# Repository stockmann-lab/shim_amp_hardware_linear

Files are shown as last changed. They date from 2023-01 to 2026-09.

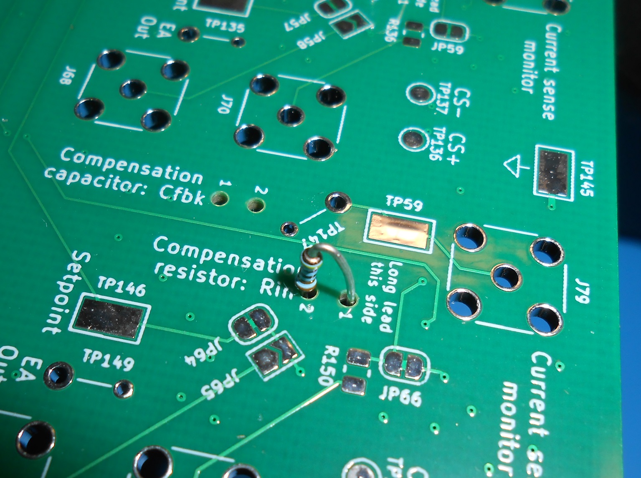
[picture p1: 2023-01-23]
docs/compensation component insertion.JPG

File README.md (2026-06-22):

# MGH open-source shim amplifier repo. 


This repo contains files related to the MGH "Revision D" linear amplifier development (and associated projects).  The shim amplifiers are designed to drive stable currents (up to 4A/channel or more if channels are ganged together in parallel) in shim coils and other inductive loads used for MRI research experiments.  The amplifiers are designed to operate inside the MRI shielded room without causing image degradation due to RF interference.

Content will include design files and bills of materials for both the Printed Circuit Boards (power board, control board, and power distribution board) as well as the mechanical enclosure.

The software and firmware for controlling the shim amplifiers via a Snickerdoodle device can be built from [https://github.com/LincolnCB/rev_d_shim](https://github.com/LincolnCB/rev_d_shim) using the [https://github.com/LincolnCB/zynq_toolbox](https://github.com/LincolnCB/zynq_toolbox) build environment repo.

More details forthcoming.

## Previous shim amplifier projects 

This project builds upon previous work done at MIT-MGH on a Class-AB linear shim amplifier that uses OPA549 op amps in a push-pull configuration.  This previous "Revision C" shim amplifier design is available at:

https://rflab.martinos.org/index.php?title=Current_driver:Current_driver

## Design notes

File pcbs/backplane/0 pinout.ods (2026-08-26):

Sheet: Programmable logic pins
Signal name | Connector pin # | FPGA pin name | FPGA pin | NOTE: I/O Vcc is 3.3V; all signals are LVCMOS
 |  |  |  | Potential problems (signals split between widely separated banks) are in red
JB2 |  |  |  | Active-low signals are preceded by ‘~’
Shutdown_Sense_Sel0 | 4 | IO_0_34 | R19 | Amplifier boards are numbered 0-7
DAC_MISO0 | 5 | IO_L23P_T3_34 | N17
ADC_MISO0 | 7 | IO_L23N_T3_34 | P18 | Signal meanings:
~LDAC0 | 6 | IO_L24N_T3_34 | P16 | SCK is the clock output from the FPGA, to each amplifier board
DAC_MOSI0 | 8 | IO_L24P_T3_34 | P15 | *_LB* are “loopback” signals returned from each amplifier board, to the FPGA (~ADC_CS, and SCK), aligned with the MISO signals
~ADC_CS_LB0 | 11 | IO_L20P_T3_34 | T17
 | 13 | IO_L20N_T3_34 | R18
ADC_MOSI0 | 12 | IO_L19N_T3_VREF_34 | R17 | Signal meanings (aux.):
~ADC_CS0 | 14 | IO_L19P_T3_34 | R16 | Shutdown sense signals, 1 per amplifier board, are latched: these are active when an individual amplifier IC activates on-die over-temp. protection, or when the FPGA forces a manual shutdown
 | 17 | IO_L21P_T3_DQS_34 | V17 | Shutdown_Sense_Sel* signals select an amplifier board’s latched shutdown sense signal to read out on Shutdown_Sense
 | 19 | IO_L21N_T3_DQS_34 | V18 | Power_Enable_FPGA enables the amplifiers when high, and forces a shutdown (and also latches every shutdown sense signal on) on every amplifier board when low
~DAC_CS0 | 18 | IO_L22N_T3_34 | W19 |  | When low, this also resets the DACs & ADCs on the amplifier boards, but only temporarily: this is not latching.
SCK0 | 20 | IO_L22P_T3_34 | W18 | ~Shutdown_Reset clears all the latched shutdown sense signals
 | 23 | IO_L15P_T2_DQS_34 | T20 | Power_Enable_Ext_Sense is high when the manual power-enable control is on, and low when off (all amp boards are forced into shutdown in this case, by backplane circuitry)
 | 25 | IO_L15N_T2_DQS_34 | U20 | Eth_SD is high when signal is detected on optical Ethernet interface
 | 24 | IO_L18N_T2_34 | W16 | Eth_Rx is received data input from optical Ethernet interface
 | 26 | IO_L18P_T2_34 | V16 | Eth_Tx is transmit data output to optical Ethernet interface
 | 29 | IO_L16P_T2_34 | V20
 | 31 | IO_L16N_T2_34 | W20
 | 30 | IO_L17N_T2_34 | Y19
 | 32 | IO_L17P_T2_34 | Y18
SCK_LB0 | 35 | IO_L14P_T2_SRCC_34 | N20
 | 37 | IO_L14N_T2_SRCC_34 | P20
Trigger_In | 36 | IO_L13N_T2_MRCC_34 | P19
10Mhz_In | 38 | IO_L13P_T2_MRCC_34 | N18
JB1
Shutdown_Sense_Sel1 | 4 | IO_25_34 | T19
ADC_MOSI1 | 5 | IO_L1P_T0_34 | T11
~DAC_CS1 | 7 | IO_L1N_T0_34 | T10
~ADC_CS1 | 6 | IO_L2N_T0_34 | U12
DAC_MISO1 | 8 | IO_L2P_T0_34 | T12
SCK1 | 11 | IO_L6P_T0_34 | P14
SCK3 | 13 | IO_L6N_T0_VREF_34 | R14
ADC_MISO1 | 12 | IO_L4N_T0_34 | W13
~ADC_CS_LB1 | 14 | IO_L4P_T0_34 | V12
~DAC_CS3 | 17 | IO_L3P_T0_DQS_PUDC_B_34 | U13
~LDAC3 | 19 | IO_L3N_T0_DQS_34 | V13
DAC_MOSI1 | 18 | IO_L5N_T0_34 | T15
~LDAC1 | 20 | IO_L5P_T0_34 | T14
DAC_MOSI3 | 23 | IO_L9P_T1_DQS_34 | T16
ADC_MOSI3 | 25 | IO_L9N_T1_DQS_34 | U17
 | 24 | IO_L7N_T1_34 | Y17
 | 26 | IO_L7P_T1_34 | Y16
~ADC_CS3 | 29 | IO_L8P_T1_34 | W14
DAC_MISO3 | 31 | IO_L8N_T1_34 | Y14
 | 30 | IO_L10N_T1_34 | W15
~ADC_CS_LB3 | 32 | IO_L10P_T1_34 | V15
SCK_LB3 | 35 | IO_L11P_T1_SRCC_34 | U14
 | 37 | IO_L11N_T1_SRCC_34 | U15
ADC_MISO3 | 36 | IO_L12N_T1_MRCC_34 | U19
SCK_LB1 | 38 | IO_L12P_T1_MRCC_34 | U18
JC1
Shutdown_Sense_Sel2 | 4 | IO_L6N_T0_VREF_13 | V5
SCK_LB2 | 5 | IO_L11P_T1_SRCC_13 | U7
ADC_MOSI2 | 7 | IO_L11N_T1_SRCC_13 | V7
SCK_LB4 | 6 | IO_L12N_T1_MRCC_13 | U10
DAC_MOSI2 | 8 | IO_L12P_T1_MRCC_13 | T9
~ADC_CS2 | 11 | IO_L19P_T3_13 | T5
~ADC_CS_LB2 | 13 | IO_L19N_T3_VREF_13 | U5
~LDAC2 | 12 | IO_L20N_T3_13 | Y13
DAC_MISO4 | 14 | IO_L20P_T3_13 | Y12
ADC_MISO2 | 17 | IO_L21P_T3_DQS_13 | V11
DAC_MISO2 | 19 | IO_L21N_T3_DQS_13 | V10
~ADC_CS_LB4 | 18 | IO_L22N_T3_13 | W6
ADC_MISO4 | 20 | IO_L22P_T3_13 | V6
SCK2 | 23 | IO_L15P_T2_DQS_13 | V8
~DAC_CS2 | 25 | IO_L15N_T2_DQS_13 | W8
~ADC_CS4 | 24 | IO_L18N_T2_13 | Y11
ADC_MOSI4 | 26 | IO_L18P_T2_13 | W11
Eth_SD | 29 | IO_L17P_T2_13 | U9
 | 31 | IO_L17N_T2_13 | U8
DAC_MOSI4 | 30 | IO_L16N_T2_13 | W9
~LDAC4 | 32 | IO_L16P_T2_13 | W10
Eth_Rx | 35 | IO_L14P_T2_SRCC_13 | Y9
Eth_Tx | 37 | IO_L14N_T2_SRCC_13 | Y8
SCK4 | 36 | IO_L13N_T2_MRCC_13 | Y6
~DAC_CS4 | 38 | IO_L13P_T2_MRCC_13 | Y7
JA2
Shutdown_Sense | 4 | IO_25_35 | J15
 | 5 | IO_L22P_T3_AD7P_35 | L14
 | 7 | IO_L22N_T3_AD7N_35 | L15
DAC_MISO6 | 6 | IO_L24N_T3_AD15N_35 | J16
~ADC_CS_LB6 | 8 | IO_L24P_T3_AD15P_35 | K16
 | 11 | IO_L23P_T3_35 | M14
 | 13 | IO_L23N_T3_35 | M15
ADC_MISO6 | 12 | IO_L19N_T3_VREF_35 | G15
~ADC_CS6 | 14 | IO_L19P_T3_35 | H15
 | 17 | IO_L21P_T3_DQS_AD14P_35 | N15
 | 19 | IO_L21N_T3_DQS_AD14N_35 | N16
ADC_MOSI6 | 18 | IO_L20N_T3_AD6N_35 | J14
DAC_MOSI6 | 20 | IO_L20P_T3_AD6P_35 | K14
 | 23 | IO_L9P_T1_DQS_AD3P_35 | L19
 | 25 | IO_L9N_T1_DQS_AD3N_35 | L20
~LDAC6 | 24 | IO_L10N_T1_AD11N_35 | J19
SCK6 | 26 | IO_L10P_T1_AD11P_35 | K19
ADC_MOSI7 | 29 | IO_L8P_T1_AD10P_35 | M17
~ADC_CS_LB7 | 31 | IO_L8N_T1_AD10N_35 | M18
~DAC_CS6 | 30 | IO_L7N_T1_AD2N_35 | M20
 | 32 | IO_L7P_T1_AD2P_35 | M19
SCK_LB7 | 35 | IO_L11P_T1_SRCC_35 | L16
 | 37 | IO_L11N_T1_SRCC_35 | L17
SCK_LB6 | 36 | IO_L12N_T1_MRCC_35 | K18
 | 38 | IO_L12P_T1_MRCC_35 | K17
JA1
~Shutdown_Reset | 4 | IO_0_35 | G14
~ADC_CS5 | 5 | IO_L5P_T0_AD9P_35 | E18
ADC_MOSI5 | 7 | IO_L5N_T0_AD9N_35 | E19
SCK7 | 6 | IO_L4N_T0_35 | D20
~DAC_CS7 | 8 | IO_L4P_T0_35 | D19
DAC_MOSI5 | 11 | IO_L6P_T0_35 | F16
~LDAC5 | 13 | IO_L6N_T0_VREF_35 | F17
~ADC_CS_LB5 | 12 | IO_L1N_T0_AD0N_35 | B20
ADC_MISO5 | 14 | IO_L1P_T0_AD0P_35 | C20
~DAC_CS5 | 17 | IO_L3P_T0_DQS_AD1P_35 | E17
Power_Enable_Ext_Sense | 19 | IO_L3N_T0_DQS_AD1N_35 | D18
DAC_MISO5 | 18 | IO_L2N_T0_AD8N_35 | A20
 | 20 | IO_L2P_T0_AD8P_35 | B19
Power_Enable_FPGA | 23 | IO_L15P_T2_DQS_AD12P_35 | F19
 | 25 | IO_L15N_T2_DQS_AD12N_35 | F20
~LDAC7 | 24 | IO_L18N_T2_AD13N_35 | G20
DAC_MOSI7 | 26 | IO_L18P_T2_AD13P_35 | G19
SCK5 | 29 | IO_L17P_T2_AD5P_35 | J20
 | 31 | IO_L17N_T2_AD5N_35 | H20
ADC_MISO7 | 30 | IO_L16N_T2_35 | G18
~ADC_CS7 | 32 | IO_L16P_T2_35 | G17
 | 35 | IO_L14P_T2_AD4P_SRCC_35 | J18
SCK_LB5 | 37 | IO_L14N_T2_AD4N_SRCC_35 | H18
DAC_MISO7 | 36 | IO_L13N_T2_MRCC_35 | H17
 | 38 | IO_L13P_T2_MRCC_35 | H16

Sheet: CPU peripheral pins
Signal name | Connector pin # | FPGA pin name | FPGA pin | Signal meanings:
 |  |  |  | UART_Tx and UART_Rx are for serial communications to host computer; Tx and Rx are from Snickerdoodle’s perspective
J3 |  |  |  | SDA and SCL are I2C bus to temperature sensors on amplifier boards; no need for clock rates higher than 100 kHz
 | 2 | PS_MIO52_501 | C10 | I2C bus connects to 2x PCA9544 bus expanders: address 1110000 handles amplifier boards 0-3, and 1110001 handles amplifier boards 4-7
 | 4 | PS_MIO53_501 | C11 | Each amplifier board has 3x ADC081C021 ADCs, with addresses 1010101 (left), 1010110 (middle), and 1011001 (right); see schematic for converting ADC readings to temperatures
 | 5 | PS_MIO16_501 | A19
 | 6 | PS_MIO19_501 | D10
 | 7 | PS_MIO17_501 | E14
 | 8 | PS_MIO18_501 | B18
 | 11 | PS_MIO20_501 | A17
 | 12 | PS_MIO23_501 | D11
 | 13 | PS_MIO21_501 | F14
 | 14 | PS_MIO22_501 | B17
 | 17 | PS_MIO24_501 | A16
 | 18 | PS_MIO27_501 | D13
 | 19 | PS_MIO25_501 | F15
 | 20 | PS_MIO26_501 | A15
 | 23 | PS_MIO28_501 | C16
 | 24 | PS_MIO31_501 | E16
 | 25 | PS_MIO29_501 | C13
 | 26 | PS_MIO30_501 | C15
 | 29 | PS_MIO32_501 | A14
 | 30 | PS_MIO35_501 | F12
 | 31 | PS_MIO33_501 | D15
 | 32 | PS_MIO34_501 | A12
UART_Tx | 35 | PS_MIO36_501 | A11
SDA | 36 | PS_MIO39_501 | C18
UART_Rx | 37 | PS_MIO37_501 | A10
SCL | 38 | PS_MIO38_501 | E13

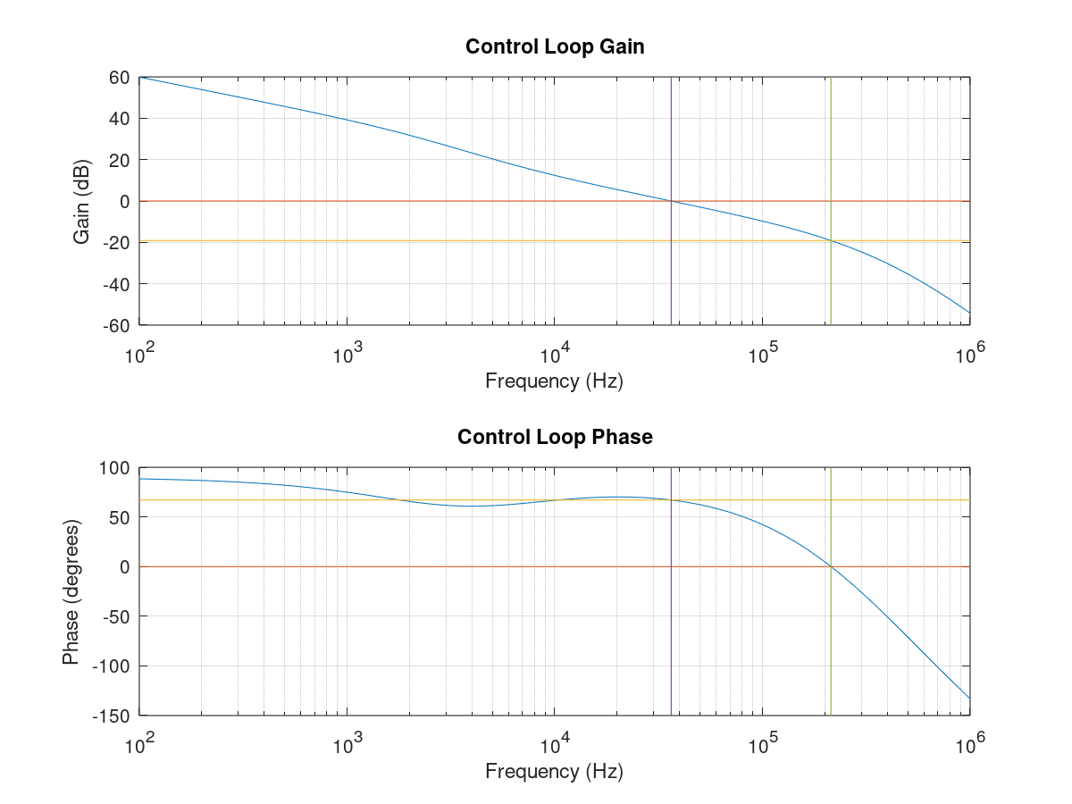
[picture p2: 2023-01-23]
docs/compensation sample output Juchem loop.png

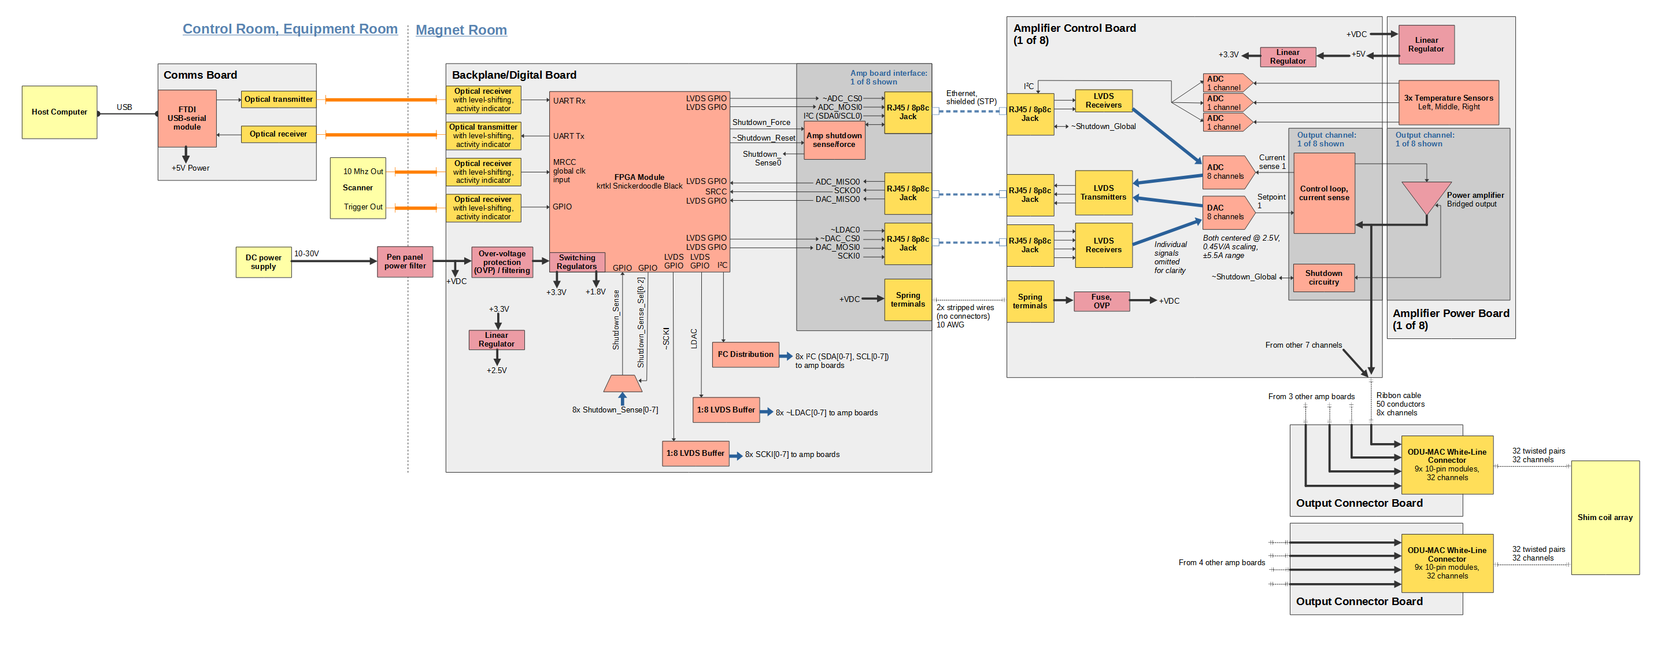
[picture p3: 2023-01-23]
docs/System block diagram.png

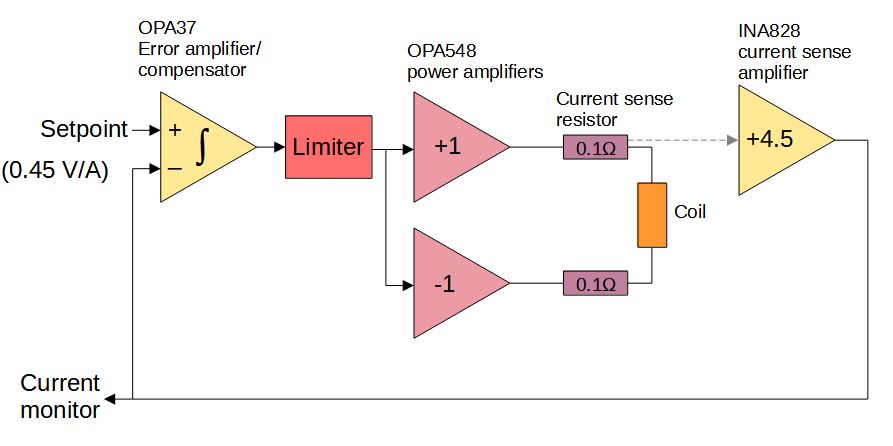
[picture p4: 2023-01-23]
docs/control loop block diagram.png

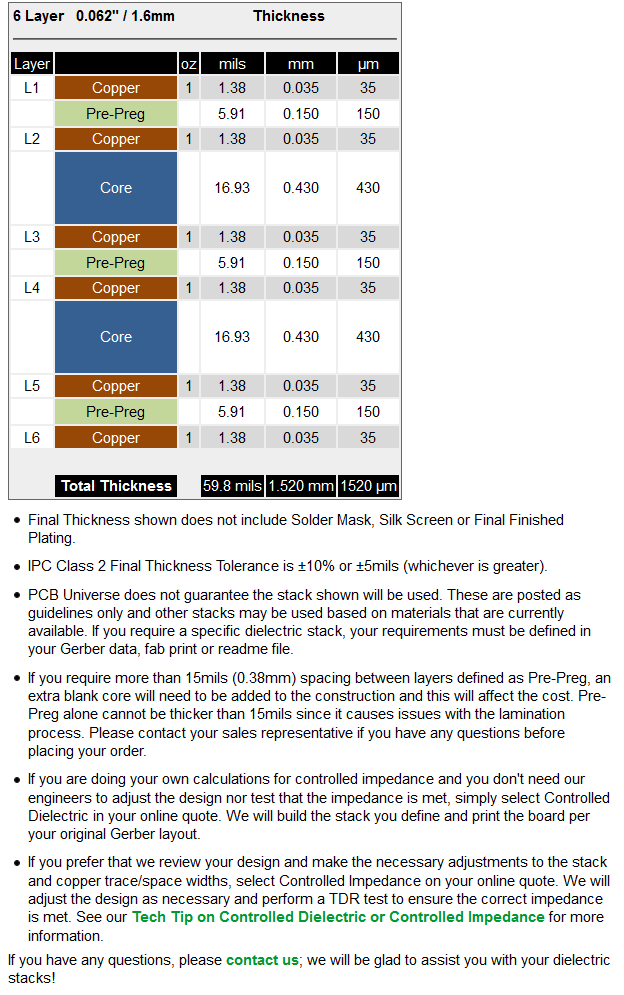
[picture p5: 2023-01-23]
pcbs/backplane/0 stackup, pcb universe.png

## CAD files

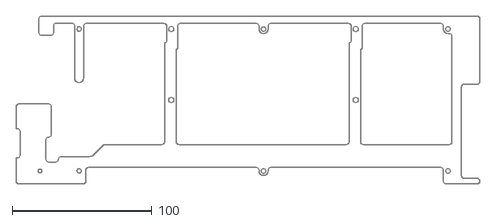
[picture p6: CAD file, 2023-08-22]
pcbs/amp ctrl/manufacturing/amp ctrl-User_StiffenerOutline.dxf
331.8 x 120.0

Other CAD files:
pcbs/amp ctrl/manufacturing/stiffener outline prelim.dxf

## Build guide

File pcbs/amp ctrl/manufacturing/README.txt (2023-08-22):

4 layers, 1.6 mm (0.062") thickness, LPI soldermask and silkscreen both sides
Outer layers 1 oz copper, inner layers 1 oz copper
ENIG plating on pads
Overall dimensions 343.25 x 120 mm (13.514" x 4.724")
Min. trace/spacing 0.16 mm (0.0063")
Min. hole size 0.26 mm (0.010")

All copper layers positive, Gerber RS-247X
*-F_Cu.gtl: Top copper layer 1 (signal)
*-In1_Cu.g2: Copper layer 2 (plane)
*-In2_Cu.g3: Copper layer 3 (plane)
*-B_Cu.gbl: Bottom copper layer 4 (signal)
*-F_Mask.gts: Top soldermask
*-B_Mask.gbs: Bottom soldermask
*-F_SilkS.gto: Top silkscreen
*-B_SilkS.gbo: Bottom silkscreen
*-Edge_Cuts.gm1: Outline
*-PTH.drl: Excellon drill file (plated holes)
*-PTH-drl_map.pdf: Drill map (plated holes)
*-NPTH.drl: Excellon drill file (non-plated holes)
*-NPTH-drl_map.pdf: Drill map (non-plated holes)

*-F_Paste.gtp: Top solder paste
*-B_Paste.gtp: Bottom solder paste
*-AssyTop.pdf: Top-side assembly drawing
*-AssyBot.pdf: Bottom-side assembly drawing
*BOM.xls: Bill of Materials
*.pos, *-pos.csv: Pick-and-place centroid file

Assembly is for bottom-side components only; all top-side components are DNP.
Some pads of DNP components are intentionally excluded from paste layer, please see solder paste Gerber files.

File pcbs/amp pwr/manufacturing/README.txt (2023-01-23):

1-layer Aluminum-core, 1.6 mm thickness with 1 W/(m*K) insulator, 1 oz copper
Lead-free (RoHS) HASL plating on pads, LPI soldermask and silkscreen on top side
Overall dimensions 290 x 110 mm (11.417" x 4.331")
Min. trace/spacing 0.2 mm (0.0079")
Min. hole size 3.2 mm (0.126")
All copper layers positive

*-Edge_Cuts.gm1: Board outline
*-F_Cu.gtl: Top copper
*-F_Mask.gts: Top soldermask
*-F_SilkS.gto: Top silkscreen
*.drl: Drill file (plated holes) - can connect to aluminum core
*-drl_map.pdf: Drill map (plated holes) - can connect to aluminum core
*-Fab.pdf: Fabrication drawing

*-AssyTop.pdf: Assembly drawing
*-F_Paste.gtp: Top solder paste
* BOM.xls: Bill of Materials
*-all.pos, *-all-pos.csv: Pick-and-place centroid component positions

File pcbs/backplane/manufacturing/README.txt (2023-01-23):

6 layers, 1.6 mm (0.062") thickness, LPI soldermask and silkscreen both sides
Outer layers 1 oz copper, inner layers 1 oz copper
ENIG plating on pads
Overall dimensions 145 x 355 mm (5.709" x 13.976")
Min. trace/spacing 0.16 mm (0.0063")
Min. hole size 0.254 mm (0.010")

All copper layers positive, Gerber RS-247X
*-F_Cu.gtl: Top copper layer 1 (mixed signal/plane)
*-In1_Cu.g2: Copper layer 2 (plane)
*-In2_Cu.g3: Copper layer 3 (mixed signal/plane)
*-In3_Cu.g4: Copper layer 4 (plane)
*-In4_Cu.g5: Copper layer 5 (mixed signal/plane)
*-B_Cu.gbl: Bottom copper layer 4 (mixed signal/plane)
*-F_Mask.gts: Top soldermask
*-B_Mask.gbs: Bottom soldermask
*-F_SilkS.gto: Top silkscreen
*-B_SilkS.gbo: Bottom silkscreen
*-Edge_Cuts.gm1: Outline
*-PTH.drl: Excellon drill file (plated holes)
*-PTH-drl_map.pdf: Drill map (plated holes)
*-NPTH.drl: Excellon drill file (non-plated holes)
*-NPTH-drl_map.pdf: Drill map (non-plated holes)

*-F_Paste.gtp: Top solder paste
*-B_Paste.gtp: Bottom solder paste
*-AssyTop.pdf: Top-side assembly drawing
*BOM.xls: Bill of Materials
*.pos, *-pos.csv: Pick-and-place centroid file

All components are on top side.
Exposed copper areas for shielding are intentionally excluded from paste layer, please see solder paste Gerber files.

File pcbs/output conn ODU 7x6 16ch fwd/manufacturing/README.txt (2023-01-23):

4 layers (1-oz copper outer and inner), 1.6 mm (0.062") thickness, LPI green soldermask and white silkscreen both sides, lead-free HASL plating on pads
Overall dimensions 68 x 104 mm (2.677" x 4.095")
All copper layers positive
Min. trace/spacing 0.18 mm (0.007")
Min. hole size > 0.5 mm (0.020")

*-F_Cu.gbr: Top (layer 1) copper
*-In1_Cu.gbr: Layer 2 copper
*-In2_Cu.gbr: Layer 3 copper
*-B_Cu.gbr: Bottom (layer 4) copper
*-F_Mask.gbr: Top soldermask
*-B_Mask.gbr: Bottom soldermask
*-F_SilkS.gbr: Top silkscreen
*-B_SilkS.gbr: Bottom silkscreen
*-Edge_Cuts.gbr: Outline
*-PTH.drl: Drill file (plated holes)
*-NPTH.drl: Drill file (non-plated holes)

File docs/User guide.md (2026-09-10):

# User guide for the linear shim amplifier

## Scaling and data format

Waveforms, as read by the "jm_tool_4board" program on the Snickerdoodle, are stored in CSV (Comma-Separated-Value) files.  There is 1 column for each channel (always with 32 columns; 64 channels are not yet supported in software) and one row per sample / timestep (1 timestep = 20 µs, or 50k samples per second).  Due to a quirk of the software, there needs to be a blank line at the end of the file to work properly.

Each data point is a number from 0 to 65535.  32768 corresponds to zero current, while lower numbers represent a negative current and higher numbers represent a positive current.  The scaling is about 0.1528 mA per count, for ±5.007A total.  The output current should not be set beyond ±4A due to limitations of the driver ICs, but the extra range is useful for reading overshoot and other transient effects.

The control voltages produced by the DAC are centered at about 2.048V (= zero current), with a range of 0-4.096V (2.048V ± 2.048V) and a scaling of 0.409 V/A, or 2.445 A/V for the output current.  When the system is idle (no current commanded through any coil), you should see 2.048V (± a couple mV) at every DAC output.

## Using external analog setpoints

Instead of using the DAC & digital controls, analog setpoints can also be sent to each channel directly through an SMA coax connector.  There are two separate modes:
(Components to populate are listed for channel 1 only on amp control board: see schematic for equivalents on other channels)
- **Without level shifter:** 2.048V = 0A, input range is 0V - 4.096V.  Populate J2, R236, R237; close jumpers JP87, JP16; open jumper JP15.
- **With level shifter:** 0V = 0A, input range is -2.048V - +2.048V.  Populate J2, R237, RN5-6, R343, C273, U73; close jumper JP16; open jumper JP15.  Signal source needs to be low-impedance, such as a 50Ω output from a function generator, to avoid creating excessive errors in offset & scaling.  If particularly low offset current is needed (under 5.6 mA), R343 can provide some adjustment range (see schematic).
In both cases, scaling is 0.4049 V/A = 2.4697 A/V.

## Misc. details for testing & development

### Connections

When powering up an incomplete system for testing, some caveats to be aware of:
- **Ethernet cable types:** Only use shielded Ethernet cables (distinguished by the metal shields on the connectors) for connecting the backplane to the amplifier boards: they use this not just for EMI, but for the backplane's control ground connection.
- **Backplane power:** The backplane gets its control-ground connection through the amplifier boards, specifically their Ethernet cables.  So if no amplifier boards are connected to the backplane via Ethernet cables, or they don't use _shielded_ Ethernet cables, then the backplane's Snickerdoodle will not have power.  For testing the backplane alone, you can connect a jumper wire from one of the amplifier-power connector's "-" sides to any of the "GND" testpoints on the backplane.  (This was done to avoid ground loops, but may be rethought after more EMI testing)
- **Amplifier control board power:** Each amplifier board stack (control & power board) has its 5V regulator, for the digital control circuitry, located on the amplifier power board for heatsinking.  If using the amplifier control board _without_ a power board attached, there will be no power to the ADC or DAC.  Either connect the amplifier control board to a power board, or make a small substitute regulator for testing, based on a 2x2 male header and a 7805 voltage regulator (see layout for pinout).

### Amplifier board final assembly

After 3rd-party assembly of all SMT parts, the through-hole parts to add manually are...
- Phoenix 1190363 **power connector** _(1x)_
- TE Connectivity 1-406541-8, or 1-406541-5, or 2-406541-1 **RJ-45 connectors** _(3x)_
See design files & BOM for component locations and details.

### Backplane board final assembly

After 3rd-party assembly of all SMT parts, the parts to add manually are...
- Phoenix 11903633 **power connectors for amplifier boards** _(1x/connected amplifier board)_
- Amphenol-ICC RJE061881120 or RJE061881120H **RJ-45 connectors** _(3x/connected amplifier board)_
- Samtec TFM-115-01-S-D-WT, or TFM-115-01-L-D-WT, or TFM-115-01-F-D-WT **Snickerdoodle connector** _(1x)_
- Samtec TFM-120-01-S-D-WT, or TFM-120-01-L-D-WT, or TFM-120-01-F-D-WT **Snickerdoodle connector** _(6x)_
- Avago AFBR-2624Z **optical receiver** _(4x)_
- Avago AFBR-1624Z **optical transmitter** _(1x)_
- ON Semi D44H11G **power transistor** _(1x)_
- CTS 7-340-1PP-BA **heatsink for power transistor** _(1x)_
See design files & BOM for component locations and details.

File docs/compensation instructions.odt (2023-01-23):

Current Drivers Rev. D

Control Loop Compensation Adjustment

Don Straney

dstraney@mgh.harvard.edu

2021-07-08

# Instructions

1. Measure the inductance and series resistance of your coil, including all cabling, using an LCR meter such as the Keysight U1733C. 100 kHz (or 10 kHz if your LCR meter doesn’t reach 100 kHz) is the preferred measurement frequency, as this is in the general range of where the control loop crossover will be.
2. Open “compensation.m” and change the values next to “Rload” and “Lload” to match your measured coil parameters.
3. If you are using MATLAB instead of GNU Octave, comment the “pkg load control” line.
4. Save and close, then run the script in MATLAB or Octave. It should produce two figures, one showing the loop frequency response and one with step response, and output text describing the component values. This is the sample output for a 723µH + 10Ω coil:

Rin total value: 108.5 ohms
Rin value to install: 8.5 ohms (closest E24 is 8.2 ohms, error of 0.3%)
Cfbk total value: 1313 pF
Cfbk value to install: 1293 pF (closest E12 is 1200 pF, error of 7.1%)
Max. load capacitance across coil: 265 pF
------------
Phase margin: 67.1 degrees @ 36360 Hz crossover
Gain margin: 19.1 dB @ 213732 Hz
------------
Min. Rin value, constrained by error amplifier BW: 108.5 ohms
Load pole: 2245.34 Hz
Error amplifier zero: 6062.42 Hz
Error amplifier GBP pole: 238797 Hz
Predicted parasitic PCB-feedback-capacitance pole: 3.97887e+06 Hz
Vout_cmd filter pole: 4.97359e+06 Hz
------------
1% settling time: 6.51e-05 s
0.1% settling time: 1.18e-04 s
1% settling time with LPF: 7.69e-05 s
0.1% settling time with LPF: 9.87e-05 s

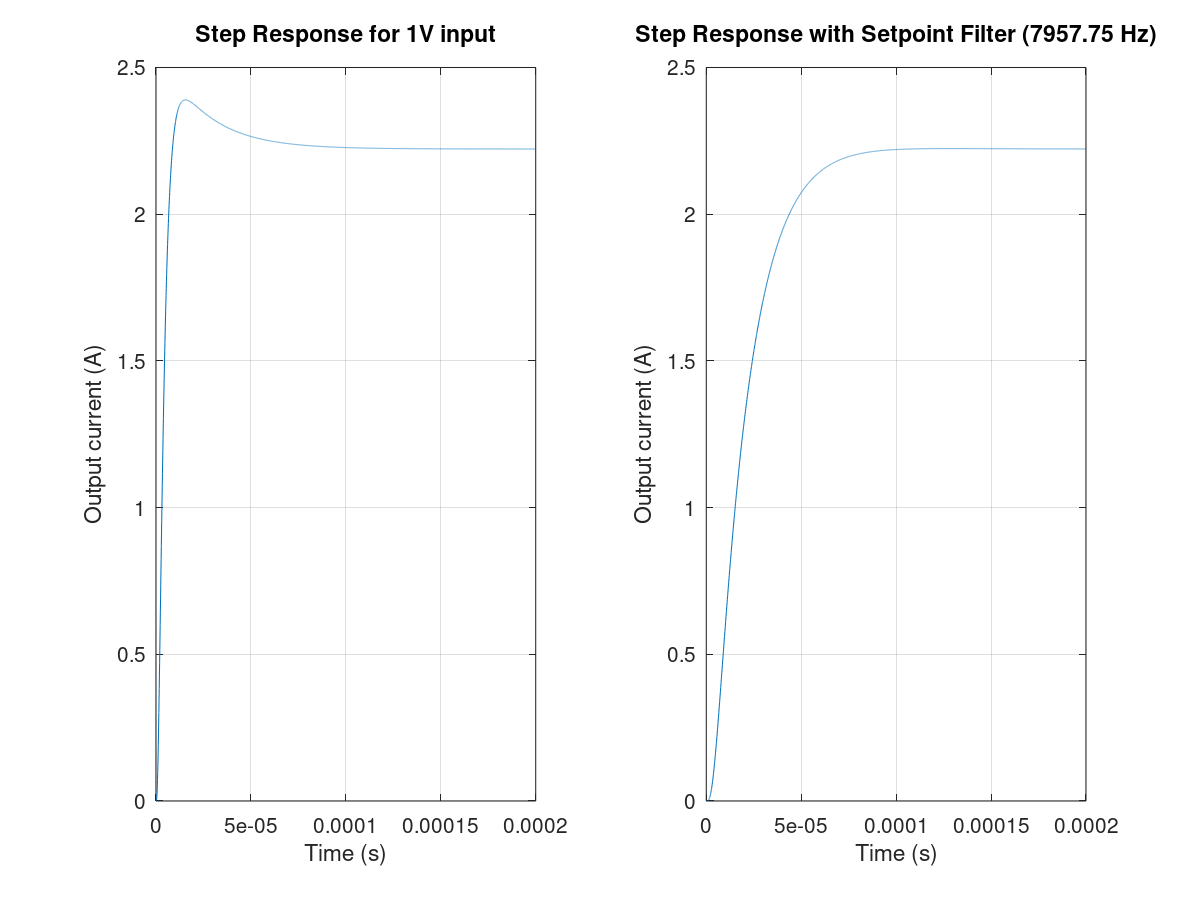
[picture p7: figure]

# Using the Results

Compensation components: There are two components you will need to install for every channel: one resistor (“Rin”) and one capacitor (“Cfbk”), with the values given here (“closest E12…” and “closest E24…”). You will need to have through-hole components with these values; for the capacitor, use 50V NP0/C0G ceramic parts with a 0.1”/2.54 mm lead spacing, and for the resistor, use a metal film (not carbon composition) 1/8W / 0204-size part for easiest insertion.

If the Cfbk value to install is < 10 pF, don’t install a capacitor. If the Rin value to install is < 5Ω, install a jumper instead (U-shaped piece of 24-26 AWG solid bare wire). Fold one of the resistor leads back over the body. Trim all leads to ~1 cm maximum away from the body.

Insert these components into the labeled sets of holes in the amp control board, from the top (outward-facing) side:

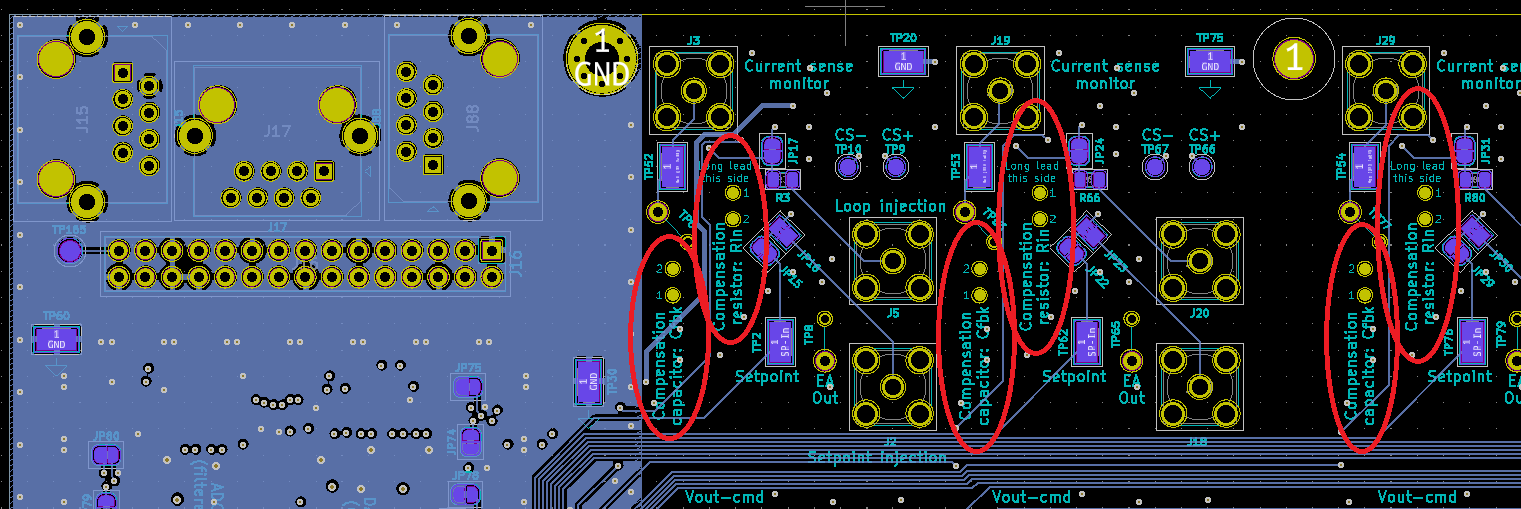
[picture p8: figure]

Make sure to insert the resistor in the orientation described, with the longer lead facing the edge of the board and the body facing the interior of the board. This orientation puts less conductor area on the inverting node of the error amplifier and potentially reduces destabilizing parasitic capacitance and coupling from other channels/noise sources.

Capacitance across coil: Shim coils will often have one or more filter capacitors placed across their leads at some point in the cabling, either to prevent transmitted RF from traveling out of the scanner’s bore along the shim cables, or to prevent RF noise outside the scanner from travelling into the bore along the shim cables. The maximum value of this capacitance is limited in practice by the resonance it creates with the shim coil’s inductance, which causes various effects that erode the gain margin and therefore stability of the control loop. The compensation script makes a general prediction of the maximum coil capacitance allowed, and prints it as “Max. load capacitance across coil” (265 pF in the example above). Do not use more than this total allowed capacitance (including feed-through filters, multiple capacitors, etc.) across your shim coil.

Settling time: The “settling time” values printed show how long it will take after each change of output current setpoint (not including the delay for digital communications) for the output current to settle to within either 1% or 0.1% of the final value.

# Slew-Rate Limiting

Some applications will want to limit the slew rate when changing the output current, to reduce the movement and auditory noise created by the force on the coil in the scanner’s magnetic field. This is best handled by software, but if for various reasons a hardware low-pass filter (LPF) is needed on the current setpoint, the effect on the step response can be predicted by the compensation script.

The “Rsplpf” and “Csplpf” variables in “compensation.m” set the parameters for a single-pole RC filter. When “compensation.m” is run, the right-most step response plot (titled “...with Setpoint Filter”) will show the modified step response with the LPF present. The second set of settling times printed (“...with LPF:”) shows the settling times with the LPF present.

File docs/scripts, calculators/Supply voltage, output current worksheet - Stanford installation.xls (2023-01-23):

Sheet: Main
Parameters
Load resistance |  |  | Calculations
Cable resistance (total) | 0.477 | Ω | Cable length | 4.5 | m | Kawin coil’s main/longest cable w/thinner wire is ~13.5’/4.5m 22 AWG and measures 0.24Ω max. per conductor
 |  |  | Wire gauge | 22 | AWG
 |  |  | Predicted cable resistance (per conductor) | 0.2385 | Ω
RF choke resistance (total) | 0.185 | Ω | RF choke resistance (each) | 0.037 | Ω | 3T toroid measured
 |  |  | Number of RF chokes, max. | 5
Coil resistance | 0.05 | Ω |  |  |  | Guess
Total load resistance | 0.712 | Ω
Shim amp
Output cable resistance (total) | 0.138 | Ω | Ribbon cable length | 0.5 | m | Overly long cable used in test setup; not far off from 0.16Ω measured (including a couple in. of 24AWG, “output connector PCB” traces, and Molex Mini-Fit Jr. connector)
 |  |  | Ribbon cable wire gauge | 28 | AWG
 |  |  | Number of parallel strands | 3
 |  |  | Predicted ribbon cable resistance (total) | 0.071 | Ω
 |  |  | Connector contact resistance (per pin) | 0.05 | Ω | Educated guess based on past measurements
 |  |  | Predicted connector resistance (total) | 0.067 | Ω
Output onboard resistance | 0.379 | Ω | Current sense resistor value | 0.1 | Ω
Total shim amp per-channel resistance | 0.517 | Ω | Total current sense resistance | 0.2 | Ω
 |  |  | PCB trace resistance (single conductor) | 0.073 |  | Worst case is channel 1: 270 mm of 1.8 mm wide traces in 1 oz copper
 |  |  | Connector contact resistance (per pin) | 0.05 |  | Educated guess based on past measurements
 |  |  | Number of parallel pins | 3
 |  |  | Total parasitic resistances to output connector | 0.179 | Ω
Power cable resistance | 0.02726666667 | Ω | Cable length | 10 | m
 |  |  | Wire gauge | 6 | AWG
 |  |  | Predicted cable resistance (per conductor) | 0.01296 | Ω
 |  |  | Backplane PCB resistance | 0.000673 | Ω | Very conservative estimate, 65 mm wide (min., wider at top) x 135 mm long (to furthest connector) on 3x 0.5 oz copper layers (at least one is actually 1 oz)
Internal power cabling resistance | 0.0052 | Ω | Cable length | 0.5 | m
Total shim amp input power resistance | 0.03246666667 | Ω | Wire gauge | 12 | AWG
 |  |  | Predicted cable resistance (per conductor) | 0.0026 | Ω
Minimum Vcc from known Iout
Desired output current per channel | 4 | A
Max. instantaneous total output current on all channels combined | 40 | A
Vcc @ OPA548 | 15.06 | V
Sag on power cable | 1.091 | V
Sag on internal power cabling | 0.208 | V
Min. Vcc | 16.4 | V

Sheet: Reference
AWG | Diameter (mm) | Ω/m
34 | 0.16 | 0.856
32 | 0.2032 | 0.538
30 | 0.254 | 0.338
28 | 0.32 | 0.213
26 | 0.404 | 0.134
24 | 0.511 | 0.084
22 | 0.645 | 0.053
20 | 0.813 | 0.033
18 | 1.024 | 0.021
16 | 1.29 | 0.013
14 | 1.628 | 0.0083
12 | 2.052 | 0.0052
10 | 2.588 | 0.0033
8 | 3.264 | 0.00206
6 | 4.115 | 0.001296
4 | 5.189 | 0.000815
2 | 6.543 | 0.000156
Extracted from OPA548 datasheet, figure 13 Fit to 3rd-order polynomial and extrapolated beyond 4A Temperature-based multiplication factor comes from increase in headroom @ 3A out (figure 14) This temperature multiplier is actually negative at a lower current (0.6A out), so may be even larger @ Iout > 3A
Output current (A) | Voltage headroom (V) | Voltage headroom @ 100 C (V) | Headroom multiplication factor:
0.1 | 1.703623124 | 1.826390744 | 1.072
0.2 | 1.773639595 | 1.901452787
0.3 | 1.842929576 | 1.975735989
0.4 | 1.911584312 | 2.049338169
0.5 | 1.979695048 | 2.122357146
0.6 | 2.047353029 | 2.19489074
0.7 | 2.114649497 | 2.267036772
0.8 | 2.181675699 | 2.33889306
0.9 | 2.248522878 | 2.410557425
1 | 2.31528228 | 2.482127687
1.1 | 2.382045147 | 2.553701665
1.2 | 2.448902726 | 2.625377178
1.3 | 2.51594626 | 2.697252048
1.4 | 2.583266994 | 2.769424093
1.5 | 2.650956172 | 2.841991134
1.6 | 2.719105039 | 2.915050989
1.7 | 2.787804839 | 2.98870148
1.8 | 2.857146816 | 3.063040425
1.9 | 2.927222216 | 3.138165645
2 | 2.998122283 | 3.214174959
2.1 | 3.06993826 | 3.291166187
2.2 | 3.142761393 | 3.369237149
2.3 | 3.216682926 | 3.448485665
2.4 | 3.291794104 | 3.529009554
2.5 | 3.36818617 | 3.610906636
2.6 | 3.44595037 | 3.694274731
2.7 | 3.525177948 | 3.779211659
2.8 | 3.605960148 | 3.865815239
2.9 | 3.688388214 | 3.954183292
3 | 3.772553392 | 4.044413637
3.1 | 3.858546926 | 4.136604093
3.2 | 3.94646006 | 4.230852482
3.3 | 4.036384038 | 4.327256622
3.4 | 4.128410106 | 4.425914333
3.5 | 4.222629507 | 4.526923435
3.6 | 4.319133486 | 4.630381747
3.7 | 4.418013287 | 4.736387091
3.8 | 4.519360156 | 4.845037284
3.9 | 4.623265335 | 4.956430148
4 | 4.729820071 | 5.070663502
4.1 | 4.839115607 | 5.187835165
4.2 | 4.951243188 | 5.308042958
4.3 | 5.066294058 | 5.4313847
4.4 | 5.184359462 | 5.557958212
4.5 | 5.305530644 | 5.687861312
4.6 | 5.429898848 | 5.82119182
4.7 | 5.55755532 | 5.958047557
4.8 | 5.688591303 | 6.098526343
4.9 | 5.823098043 | 6.242725996
5 | 5.961166783 | 6.390744337

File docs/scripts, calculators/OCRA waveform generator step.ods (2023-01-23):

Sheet: Params
Amplitude | -1.5 | A
Length | 2.00E-02 | sec
Length, calculated | 999 | samples
Channel #, min. | 8 | (1-32)
Channel #, max. | 8 | (1-32)
Timestep | 2.00E-05 | sec
Vref | 2.5 | V
Scaling factor | 0.449201 | V/A
NOTE: Tab separators are ok, but output file needs space at end of last text line

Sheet: Amplitudes (A)
0 | 0 | 0 | 0 | 0 | 0 | 0 | -1.5 | 0 | 0 | 0 | 0 | 0 | 0 | 0 | 0 | 0 | 0 | 0 | 0 | 0 | 0 | 0 | 0 | 0 | 0 | 0 | 0 | 0 | 0 | 0 | 0
0 | 0 | 0 | 0 | 0 | 0 | 0 | -1.5 | 0 | 0 | 0 | 0 | 0 | 0 | 0 | 0 | 0 | 0 | 0 | 0 | 0 | 0 | 0 | 0 | 0 | 0 | 0 | 0 | 0 | 0 | 0 | 0
0 | 0 | 0 | 0 | 0 | 0 | 0 | -1.5 | 0 | 0 | 0 | 0 | 0 | 0 | 0 | 0 | 0 | 0 | 0 | 0 | 0 | 0 | 0 | 0 | 0 | 0 | 0 | 0 | 0 | 0 | 0 | 0
0 | 0 | 0 | 0 | 0 | 0 | 0 | -1.5 | 0 | 0 | 0 | 0 | 0 | 0 | 0 | 0 | 0 | 0 | 0 | 0 | 0 | 0 | 0 | 0 | 0 | 0 | 0 | 0 | 0 | 0 | 0 | 0
0 | 0 | 0 | 0 | 0 | 0 | 0 | -1.5 | 0 | 0 | 0 | 0 | 0 | 0 | 0 | 0 | 0 | 0 | 0 | 0 | 0 | 0 | 0 | 0 | 0 | 0 | 0 | 0 | 0 | 0 | 0 | 0
0 | 0 | 0 | 0 | 0 | 0 | 0 | -1.5 | 0 | 0 | 0 | 0 | 0 | 0 | 0 | 0 | 0 | 0 | 0 | 0 | 0 | 0 | 0 | 0 | 0 | 0 | 0 | 0 | 0 | 0 | 0 | 0
0 | 0 | 0 | 0 | 0 | 0 | 0 | -1.5 | 0 | 0 | 0 | 0 | 0 | 0 | 0 | 0 | 0 | 0 | 0 | 0 | 0 | 0 | 0 | 0 | 0 | 0 | 0 | 0 | 0 | 0 | 0 | 0
0 | 0 | 0 | 0 | 0 | 0 | 0 | -1.5 | 0 | 0 | 0 | 0 | 0 | 0 | 0 | 0 | 0 | 0 | 0 | 0 | 0 | 0 | 0 | 0 | 0 | 0 | 0 | 0 | 0 | 0 | 0 | 0
0 | 0 | 0 | 0 | 0 | 0 | 0 | -1.5 | 0 | 0 | 0 | 0 | 0 | 0 | 0 | 0 | 0 | 0 | 0 | 0 | 0 | 0 | 0 | 0 | 0 | 0 | 0 | 0 | 0 | 0 | 0 | 0
0 | 0 | 0 | 0 | 0 | 0 | 0 | -1.5 | 0 | 0 | 0 | 0 | 0 | 0 | 0 | 0 | 0 | 0 | 0 | 0 | 0 | 0 | 0 | 0 | 0 | 0 | 0 | 0 | 0 | 0 | 0 | 0
0 | 0 | 0 | 0 | 0 | 0 | 0 | -1.5 | 0 | 0 | 0 | 0 | 0 | 0 | 0 | 0 | 0 | 0 | 0 | 0 | 0 | 0 | 0 | 0 | 0 | 0 | 0 | 0 | 0 | 0 | 0 | 0
0 | 0 | 0 | 0 | 0 | 0 | 0 | -1.5 | 0 | 0 | 0 | 0 | 0 | 0 | 0 | 0 | 0 | 0 | 0 | 0 | 0 | 0 | 0 | 0 | 0 | 0 | 0 | 0 | 0 | 0 | 0 | 0
0 | 0 | 0 | 0 | 0 | 0 | 0 | -1.5 | 0 | 0 | 0 | 0 | 0 | 0 | 0 | 0 | 0 | 0 | 0 | 0 | 0 | 0 | 0 | 0 | 0 | 0 | 0 | 0 | 0 | 0 | 0 | 0
0 | 0 | 0 | 0 | 0 | 0 | 0 | -1.5 | 0 | 0 | 0 | 0 | 0 | 0 | 0 | 0 | 0 | 0 | 0 | 0 | 0 | 0 | 0 | 0 | 0 | 0 | 0 | 0 | 0 | 0 | 0 | 0
0 | 0 | 0 | 0 | 0 | 0 | 0 | -1.5 | 0 | 0 | 0 | 0 | 0 | 0 | 0 | 0 | 0 | 0 | 0 | 0 | 0 | 0 | 0 | 0 | 0 | 0 | 0 | 0 | 0 | 0 | 0 | 0
0 | 0 | 0 | 0 | 0 | 0 | 0 | -1.5 | 0 | 0 | 0 | 0 | 0 | 0 | 0 | 0 | 0 | 0 | 0 | 0 | 0 | 0 | 0 | 0 | 0 | 0 | 0 | 0 | 0 | 0 | 0 | 0
0 | 0 | 0 | 0 | 0 | 0 | 0 | -1.5 | 0 | 0 | 0 | 0 | 0 | 0 | 0 | 0 | 0 | 0 | 0 | 0 | 0 | 0 | 0 | 0 | 0 | 0 | 0 | 0 | 0 | 0 | 0 | 0
0 | 0 | 0 | 0 | 0 | 0 | 0 | -1.5 | 0 | 0 | 0 | 0 | 0 | 0 | 0 | 0 | 0 | 0 | 0 | 0 | 0 | 0 | 0 | 0 | 0 | 0 | 0 | 0 | 0 | 0 | 0 | 0
0 | 0 | 0 | 0 | 0 | 0 | 0 | -1.5 | 0 | 0 | 0 | 0 | 0 | 0 | 0 | 0 | 0 | 0 | 0 | 0 | 0 | 0 | 0 | 0 | 0 | 0 | 0 | 0 | 0 | 0 | 0 | 0
0 | 0 | 0 | 0 | 0 | 0 | 0 | -1.5 | 0 | 0 | 0 | 0 | 0 | 0 | 0 | 0 | 0 | 0 | 0 | 0 | 0 | 0 | 0 | 0 | 0 | 0 | 0 | 0 | 0 | 0 | 0 | 0
0 | 0 | 0 | 0 | 0 | 0 | 0 | -1.5 | 0 | 0 | 0 | 0 | 0 | 0 | 0 | 0 | 0 | 0 | 0 | 0 | 0 | 0 | 0 | 0 | 0 | 0 | 0 | 0 | 0 | 0 | 0 | 0
0 | 0 | 0 | 0 | 0 | 0 | 0 | -1.5 | 0 | 0 | 0 | 0 | 0 | 0 | 0 | 0 | 0 | 0 | 0 | 0 | 0 | 0 | 0 | 0 | 0 | 0 | 0 | 0 | 0 | 0 | 0 | 0
0 | 0 | 0 | 0 | 0 | 0 | 0 | -1.5 | 0 | 0 | 0 | 0 | 0 | 0 | 0 | 0 | 0 | 0 | 0 | 0 | 0 | 0 | 0 | 0 | 0 | 0 | 0 | 0 | 0 | 0 | 0 | 0
0 | 0 | 0 | 0 | 0 | 0 | 0 | -1.5 | 0 | 0 | 0 | 0 | 0 | 0 | 0 | 0 | 0 | 0 | 0 | 0 | 0 | 0 | 0 | 0 | 0 | 0 | 0 | 0 | 0 | 0 | 0 | 0
0 | 0 | 0 | 0 | 0 | 0 | 0 | -1.5 | 0 | 0 | 0 | 0 | 0 | 0 | 0 | 0 | 0 | 0 | 0 | 0 | 0 | 0 | 0 | 0 | 0 | 0 | 0 | 0 | 0 | 0 | 0 | 0
0 | 0 | 0 | 0 | 0 | 0 | 0 | -1.5 | 0 | 0 | 0 | 0 | 0 | 0 | 0 | 0 | 0 | 0 | 0 | 0 | 0 | 0 | 0 | 0 | 0 | 0 | 0 | 0 | 0 | 0 | 0 | 0
0 | 0 | 0 | 0 | 0 | 0 | 0 | -1.5 | 0 | 0 | 0 | 0 | 0 | 0 | 0 | 0 | 0 | 0 | 0 | 0 | 0 | 0 | 0 | 0 | 0 | 0 | 0 | 0 | 0 | 0 | 0 | 0
0 | 0 | 0 | 0 | 0 | 0 | 0 | -1.5 | 0 | 0 | 0 | 0 | 0 | 0 | 0 | 0 | 0 | 0 | 0 | 0 | 0 | 0 | 0 | 0 | 0 | 0 | 0 | 0 | 0 | 0 | 0 | 0
0 | 0 | 0 | 0 | 0 | 0 | 0 | -1.5 | 0 | 0 | 0 | 0 | 0 | 0 | 0 | 0 | 0 | 0 | 0 | 0 | 0 | 0 | 0 | 0 | 0 | 0 | 0 | 0 | 0 | 0 | 0 | 0
0 | 0 | 0 | 0 | 0 | 0 | 0 | -1.5 | 0 | 0 | 0 | 0 | 0 | 0 | 0 | 0 | 0 | 0 | 0 | 0 | 0 | 0 | 0 | 0 | 0 | 0 | 0 | 0 | 0 | 0 | 0 | 0
0 | 0 | 0 | 0 | 0 | 0 | 0 | -1.5 | 0 | 0 | 0 | 0 | 0 | 0 | 0 | 0 | 0 | 0 | 0 | 0 | 0 | 0 | 0 | 0 | 0 | 0 | 0 | 0 | 0 | 0 | 0 | 0
0 | 0 | 0 | 0 | 0 | 0 | 0 | -1.5 | 0 | 0 | 0 | 0 | 0 | 0 | 0 | 0 | 0 | 0 | 0 | 0 | 0 | 0 | 0 | 0 | 0 | 0 | 0 | 0 | 0 | 0 | 0 | 0
0 | 0 | 0 | 0 | 0 | 0 | 0 | -1.5 | 0 | 0 | 0 | 0 | 0 | 0 | 0 | 0 | 0 | 0 | 0 | 0 | 0 | 0 | 0 | 0 | 0 | 0 | 0 | 0 | 0 | 0 | 0 | 0
0 | 0 | 0 | 0 | 0 | 0 | 0 | -1.5 | 0 | 0 | 0 | 0 | 0 | 0 | 0 | 0 | 0 | 0 | 0 | 0 | 0 | 0 | 0 | 0 | 0 | 0 | 0 | 0 | 0 | 0 | 0 | 0
0 | 0 | 0 | 0 | 0 | 0 | 0 | -1.5 | 0 | 0 | 0 | 0 | 0 | 0 | 0 | 0 | 0 | 0 | 0 | 0 | 0 | 0 | 0 | 0 | 0 | 0 | 0 | 0 | 0 | 0 | 0 | 0
0 | 0 | 0 | 0 | 0 | 0 | 0 | -1.5 | 0 | 0 | 0 | 0 | 0 | 0 | 0 | 0 | 0 | 0 | 0 | 0 | 0 | 0 | 0 | 0 | 0 | 0 | 0 | 0 | 0 | 0 | 0 | 0
0 | 0 | 0 | 0 | 0 | 0 | 0 | -1.5 | 0 | 0 | 0 | 0 | 0 | 0 | 0 | 0 | 0 | 0 | 0 | 0 | 0 | 0 | 0 | 0 | 0 | 0 | 0 | 0 | 0 | 0 | 0 | 0
0 | 0 | 0 | 0 | 0 | 0 | 0 | -1.5 | 0 | 0 | 0 | 0 | 0 | 0 | 0 | 0 | 0 | 0 | 0 | 0 | 0 | 0 | 0 | 0 | 0 | 0 | 0 | 0 | 0 | 0 | 0 | 0
0 | 0 | 0 | 0 | 0 | 0 | 0 | -1.5 | 0 | 0 | 0 | 0 | 0 | 0 | 0 | 0 | 0 | 0 | 0 | 0 | 0 | 0 | 0 | 0 | 0 | 0 | 0 | 0 | 0 | 0 | 0 | 0
0 | 0 | 0 | 0 | 0 | 0 | 0 | -1.5 | 0 | 0 | 0 | 0 | 0 | 0 | 0 | 0 | 0 | 0 | 0 | 0 | 0 | 0 | 0 | 0 | 0 | 0 | 0 | 0 | 0 | 0 | 0 | 0
0 | 0 | 0 | 0 | 0 | 0 | 0 | -1.5 | 0 | 0 | 0 | 0 | 0 | 0 | 0 | 0 | 0 | 0 | 0 | 0 | 0 | 0 | 0 | 0 | 0 | 0 | 0 | 0 | 0 | 0 | 0 | 0
0 | 0 | 0 | 0 | 0 | 0 | 0 | -1.5 | 0 | 0 | 0 | 0 | 0 | 0 | 0 | 0 | 0 | 0 | 0 | 0 | 0 | 0 | 0 | 0 | 0 | 0 | 0 | 0 | 0 | 0 | 0 | 0
0 | 0 | 0 | 0 | 0 | 0 | 0 | -1.5 | 0 | 0 | 0 | 0 | 0 | 0 | 0 | 0 | 0 | 0 | 0 | 0 | 0 | 0 | 0 | 0 | 0 | 0 | 0 | 0 | 0 | 0 | 0 | 0
0 | 0 | 0 | 0 | 0 | 0 | 0 | -1.5 | 0 | 0 | 0 | 0 | 0 | 0 | 0 | 0 | 0 | 0 | 0 | 0 | 0 | 0 | 0 | 0 | 0 | 0 | 0 | 0 | 0 | 0 | 0 | 0
0 | 0 | 0 | 0 | 0 | 0 | 0 | -1.5 | 0 | 0 | 0 | 0 | 0 | 0 | 0 | 0 | 0 | 0 | 0 | 0 | 0 | 0 | 0 | 0 | 0 | 0 | 0 | 0 | 0 | 0 | 0 | 0
0 | 0 | 0 | 0 | 0 | 0 | 0 | -1.5 | 0 | 0 | 0 | 0 | 0 | 0 | 0 | 0 | 0 | 0 | 0 | 0 | 0 | 0 | 0 | 0 | 0 | 0 | 0 | 0 | 0 | 0 | 0 | 0
0 | 0 | 0 | 0 | 0 | 0 | 0 | -1.5 | 0 | 0 | 0 | 0 | 0 | 0 | 0 | 0 | 0 | 0 | 0 | 0 | 0 | 0 | 0 | 0 | 0 | 0 | 0 | 0 | 0 | 0 | 0 | 0
0 | 0 | 0 | 0 | 0 | 0 | 0 | -1.5 | 0 | 0 | 0 | 0 | 0 | 0 | 0 | 0 | 0 | 0 | 0 | 0 | 0 | 0 | 0 | 0 | 0 | 0 | 0 | 0 | 0 | 0 | 0 | 0
0 | 0 | 0 | 0 | 0 | 0 | 0 | -1.5 | 0 | 0 | 0 | 0 | 0 | 0 | 0 | 0 | 0 | 0 | 0 | 0 | 0 | 0 | 0 | 0 | 0 | 0 | 0 | 0 | 0 | 0 | 0 | 0
0 | 0 | 0 | 0 | 0 | 0 | 0 | -1.5 | 0 | 0 | 0 | 0 | 0 | 0 | 0 | 0 | 0 | 0 | 0 | 0 | 0 | 0 | 0 | 0 | 0 | 0 | 0 | 0 | 0 | 0 | 0 | 0
0 | 0 | 0 | 0 | 0 | 0 | 0 | -1.5 | 0 | 0 | 0 | 0 | 0 | 0 | 0 | 0 | 0 | 0 | 0 | 0 | 0 | 0 | 0 | 0 | 0 | 0 | 0 | 0 | 0 | 0 | 0 | 0
0 | 0 | 0 | 0 | 0 | 0 | 0 | -1.5 | 0 | 0 | 0 | 0 | 0 | 0 | 0 | 0 | 0 | 0 | 0 | 0 | 0 | 0 | 0 | 0 | 0 | 0 | 0 | 0 | 0 | 0 | 0 | 0
0 | 0 | 0 | 0 | 0 | 0 | 0 | -1.5 | 0 | 0 | 0 | 0 | 0 | 0 | 0 | 0 | 0 | 0 | 0 | 0 | 0 | 0 | 0 | 0 | 0 | 0 | 0 | 0 | 0 | 0 | 0 | 0
0 | 0 | 0 | 0 | 0 | 0 | 0 | -1.5 | 0 | 0 | 0 | 0 | 0 | 0 | 0 | 0 | 0 | 0 | 0 | 0 | 0 | 0 | 0 | 0 | 0 | 0 | 0 | 0 | 0 | 0 | 0 | 0
0 | 0 | 0 | 0 | 0 | 0 | 0 | -1.5 | 0 | 0 | 0 | 0 | 0 | 0 | 0 | 0 | 0 | 0 | 0 | 0 | 0 | 0 | 0 | 0 | 0 | 0 | 0 | 0 | 0 | 0 | 0 | 0
0 | 0 | 0 | 0 | 0 | 0 | 0 | -1.5 | 0 | 0 | 0 | 0 | 0 | 0 | 0 | 0 | 0 | 0 | 0 | 0 | 0 | 0 | 0 | 0 | 0 | 0 | 0 | 0 | 0 | 0 | 0 | 0
0 | 0 | 0 | 0 | 0 | 0 | 0 | -1.5 | 0 | 0 | 0 | 0 | 0 | 0 | 0 | 0 | 0 | 0 | 0 | 0 | 0 | 0 | 0 | 0 | 0 | 0 | 0 | 0 | 0 | 0 | 0 | 0
0 | 0 | 0 | 0 | 0 | 0 | 0 | -1.5 | 0 | 0 | 0 | 0 | 0 | 0 | 0 | 0 | 0 | 0 | 0 | 0 | 0 | 0 | 0 | 0 | 0 | 0 | 0 | 0 | 0 | 0 | 0 | 0
0 | 0 | 0 | 0 | 0 | 0 | 0 | -1.5 | 0 | 0 | 0 | 0 | 0 | 0 | 0 | 0 | 0 | 0 | 0 | 0 | 0 | 0 | 0 | 0 | 0 | 0 | 0 | 0 | 0 | 0 | 0 | 0
0 | 0 | 0 | 0 | 0 | 0 | 0 | -1.5 | 0 | 0 | 0 | 0 | 0 | 0 | 0 | 0 | 0 | 0 | 0 | 0 | 0 | 0 | 0 | 0 | 0 | 0 | 0 | 0 | 0 | 0 | 0 | 0
0 | 0 | 0 | 0 | 0 | 0 | 0 | -1.5 | 0 | 0 | 0 | 0 | 0 | 0 | 0 | 0 | 0 | 0 | 0 | 0 | 0 | 0 | 0 | 0 | 0 | 0 | 0 | 0 | 0 | 0 | 0 | 0
0 | 0 | 0 | 0 | 0 | 0 | 0 | -1.5 | 0 | 0 | 0 | 0 | 0 | 0 | 0 | 0 | 0 | 0 | 0 | 0 | 0 | 0 | 0 | 0 | 0 | 0 | 0 | 0 | 0 | 0 | 0 | 0
0 | 0 | 0 | 0 | 0 | 0 | 0 | -1.5 | 0 | 0 | 0 | 0 | 0 | 0 | 0 | 0 | 0 | 0 | 0 | 0 | 0 | 0 | 0 | 0 | 0 | 0 | 0 | 0 | 0 | 0 | 0 | 0
0 | 0 | 0 | 0 | 0 | 0 | 0 | -1.5 | 0 | 0 | 0 | 0 | 0 | 0 | 0 | 0 | 0 | 0 | 0 | 0 | 0 | 0 | 0 | 0 | 0 | 0 | 0 | 0 | 0 | 0 | 0 | 0
0 | 0 | 0 | 0 | 0 | 0 | 0 | -1.5 | 0 | 0 | 0 | 0 | 0 | 0 | 0 | 0 | 0 | 0 | 0 | 0 | 0 | 0 | 0 | 0 | 0 | 0 | 0 | 0 | 0 | 0 | 0 | 0
0 | 0 | 0 | 0 | 0 | 0 | 0 | -1.5 | 0 | 0 | 0 | 0 | 0 | 0 | 0 | 0 | 0 | 0 | 0 | 0 | 0 | 0 | 0 | 0 | 0 | 0 | 0 | 0 | 0 | 0 | 0 | 0
0 | 0 | 0 | 0 | 0 | 0 | 0 | -1.5 | 0 | 0 | 0 | 0 | 0 | 0 | 0 | 0 | 0 | 0 | 0 | 0 | 0 | 0 | 0 | 0 | 0 | 0 | 0 | 0 | 0 | 0 | 0 | 0
0 | 0 | 0 | 0 | 0 | 0 | 0 | -1.5 | 0 | 0 | 0 | 0 | 0 | 0 | 0 | 0 | 0 | 0 | 0 | 0 | 0 | 0 | 0 | 0 | 0 | 0 | 0 | 0 | 0 | 0 | 0 | 0
0 | 0 | 0 | 0 | 0 | 0 | 0 | -1.5 | 0 | 0 | 0 | 0 | 0 | 0 | 0 | 0 | 0 | 0 | 0 | 0 | 0 | 0 | 0 | 0 | 0 | 0 | 0 | 0 | 0 | 0 | 0 | 0
0 | 0 | 0 | 0 | 0 | 0 | 0 | -1.5 | 0 | 0 | 0 | 0 | 0 | 0 | 0 | 0 | 0 | 0 | 0 | 0 | 0 | 0 | 0 | 0 | 0 | 0 | 0 | 0 | 0 | 0 | 0 | 0
0 | 0 | 0 | 0 | 0 | 0 | 0 | -1.5 | 0 | 0 | 0 | 0 | 0 | 0 | 0 | 0 | 0 | 0 | 0 | 0 | 0 | 0 | 0 | 0 | 0 | 0 | 0 | 0 | 0 | 0 | 0 | 0
0 | 0 | 0 | 0 | 0 | 0 | 0 | -1.5 | 0 | 0 | 0 | 0 | 0 | 0 | 0 | 0 | 0 | 0 | 0 | 0 | 0 | 0 | 0 | 0 | 0 | 0 | 0 | 0 | 0 | 0 | 0 | 0
0 | 0 | 0 | 0 | 0 | 0 | 0 | -1.5 | 0 | 0 | 0 | 0 | 0 | 0 | 0 | 0 | 0 | 0 | 0 | 0 | 0 | 0 | 0 | 0 | 0 | 0 | 0 | 0 | 0 | 0 | 0 | 0
0 | 0 | 0 | 0 | 0 | 0 | 0 | -1.5 | 0 | 0 | 0 | 0 | 0 | 0 | 0 | 0 | 0 | 0 | 0 | 0 | 0 | 0 | 0 | 0 | 0 | 0 | 0 | 0 | 0 | 0 | 0 | 0
0 | 0 | 0 | 0 | 0 | 0 | 0 | -1.5 | 0 | 0 | 0 | 0 | 0 | 0 | 0 | 0 | 0 | 0 | 0 | 0 | 0 | 0 | 0 | 0 | 0 | 0 | 0 | 0 | 0 | 0 | 0 | 0
0 | 0 | 0 | 0 | 0 | 0 | 0 | -1.5 | 0 | 0 | 0 | 0 | 0 | 0 | 0 | 0 | 0 | 0 | 0 | 0 | 0 | 0 | 0 | 0 | 0 | 0 | 0 | 0 | 0 | 0 | 0 | 0
0 | 0 | 0 | 0 | 0 | 0 | 0 | -1.5 | 0 | 0 | 0 | 0 | 0 | 0 | 0 | 0 | 0 | 0 | 0 | 0 | 0 | 0 | 0 | 0 | 0 | 0 | 0 | 0 | 0 | 0 | 0 | 0
0 | 0 | 0 | 0 | 0 | 0 | 0 | -1.5 | 0 | 0 | 0 | 0 | 0 | 0 | 0 | 0 | 0 | 0 | 0 | 0 | 0 | 0 | 0 | 0 | 0 | 0 | 0 | 0 | 0 | 0 | 0 | 0
0 | 0 | 0 | 0 | 0 | 0 | 0 | -1.5 | 0 | 0 | 0 | 0 | 0 | 0 | 0 | 0 | 0 | 0 | 0 | 0 | 0 | 0 | 0 | 0 | 0 | 0 | 0 | 0 | 0 | 0 | 0 | 0
0 | 0 | 0 | 0 | 0 | 0 | 0 | -1.5 | 0 | 0 | 0 | 0 | 0 | 0 | 0 | 0 | 0 | 0 | 0 | 0 | 0 | 0 | 0 | 0 | 0 | 0 | 0 | 0 | 0 | 0 | 0 | 0
0 | 0 | 0 | 0 | 0 | 0 | 0 | -1.5 | 0 | 0 | 0 | 0 | 0 | 0 | 0 | 0 | 0 | 0 | 0 | 0 | 0 | 0 | 0 | 0 | 0 | 0 | 0 | 0 | 0 | 0 | 0 | 0
0 | 0 | 0 | 0 | 0 | 0 | 0 | -1.5 | 0 | 0 | 0 | 0 | 0 | 0 | 0 | 0 | 0 | 0 | 0 | 0 | 0 | 0 | 0 | 0 | 0 | 0 | 0 | 0 | 0 | 0 | 0 | 0
0 | 0 | 0 | 0 | 0 | 0 | 0 | -1.5 | 0 | 0 | 0 | 0 | 0 | 0 | 0 | 0 | 0 | 0 | 0 | 0 | 0 | 0 | 0 | 0 | 0 | 0 | 0 | 0 | 0 | 0 | 0 | 0
0 | 0 | 0 | 0 | 0 | 0 | 0 | -1.5 | 0 | 0 | 0 | 0 | 0 | 0 | 0 | 0 | 0 | 0 | 0 | 0 | 0 | 0 | 0 | 0 | 0 | 0 | 0 | 0 | 0 | 0 | 0 | 0
0 | 0 | 0 | 0 | 0 | 0 | 0 | -1.5 | 0 | 0 | 0 | 0 | 0 | 0 | 0 | 0 | 0 | 0 | 0 | 0 | 0 | 0 | 0 | 0 | 0 | 0 | 0 | 0 | 0 | 0 | 0 | 0
0 | 0 | 0 | 0 | 0 | 0 | 0 | -1.5 | 0 | 0 | 0 | 0 | 0 | 0 | 0 | 0 | 0 | 0 | 0 | 0 | 0 | 0 | 0 | 0 | 0 | 0 | 0 | 0 | 0 | 0 | 0 | 0
0 | 0 | 0 | 0 | 0 | 0 | 0 | -1.5 | 0 | 0 | 0 | 0 | 0 | 0 | 0 | 0 | 0 | 0 | 0 | 0 | 0 | 0 | 0 | 0 | 0 | 0 | 0 | 0 | 0 | 0 | 0 | 0
0 | 0 | 0 | 0 | 0 | 0 | 0 | -1.5 | 0 | 0 | 0 | 0 | 0 | 0 | 0 | 0 | 0 | 0 | 0 | 0 | 0 | 0 | 0 | 0 | 0 | 0 | 0 | 0 | 0 | 0 | 0 | 0
0 | 0 | 0 | 0 | 0 | 0 | 0 | -1.5 | 0 | 0 | 0 | 0 | 0 | 0 | 0 | 0 | 0 | 0 | 0 | 0 | 0 | 0 | 0 | 0 | 0 | 0 | 0 | 0 | 0 | 0 | 0 | 0
0 | 0 | 0 | 0 | 0 | 0 | 0 | -1.5 | 0 | 0 | 0 | 0 | 0 | 0 | 0 | 0 | 0 | 0 | 0 | 0 | 0 | 0 | 0 | 0 | 0 | 0 | 0 | 0 | 0 | 0 | 0 | 0
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

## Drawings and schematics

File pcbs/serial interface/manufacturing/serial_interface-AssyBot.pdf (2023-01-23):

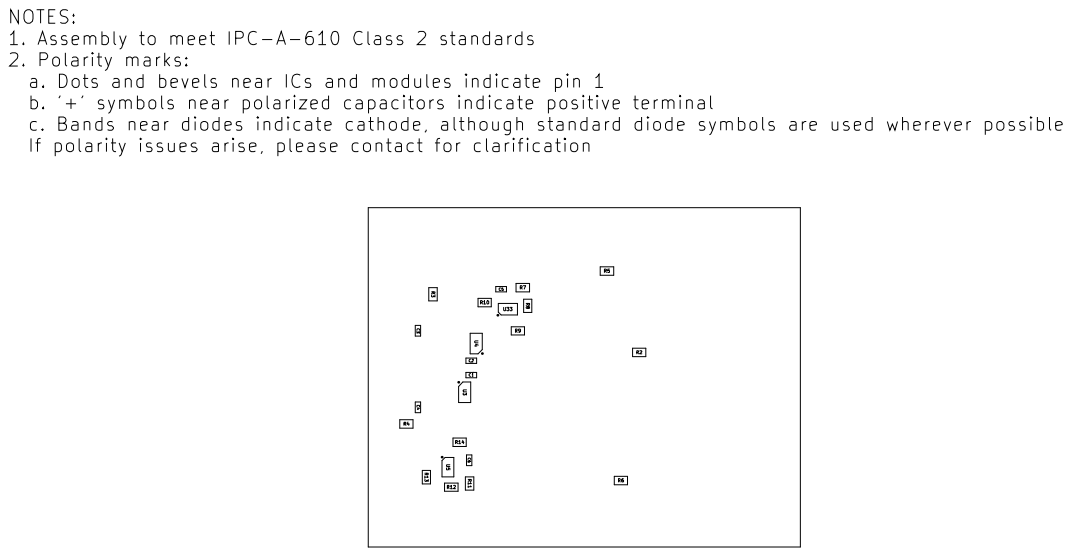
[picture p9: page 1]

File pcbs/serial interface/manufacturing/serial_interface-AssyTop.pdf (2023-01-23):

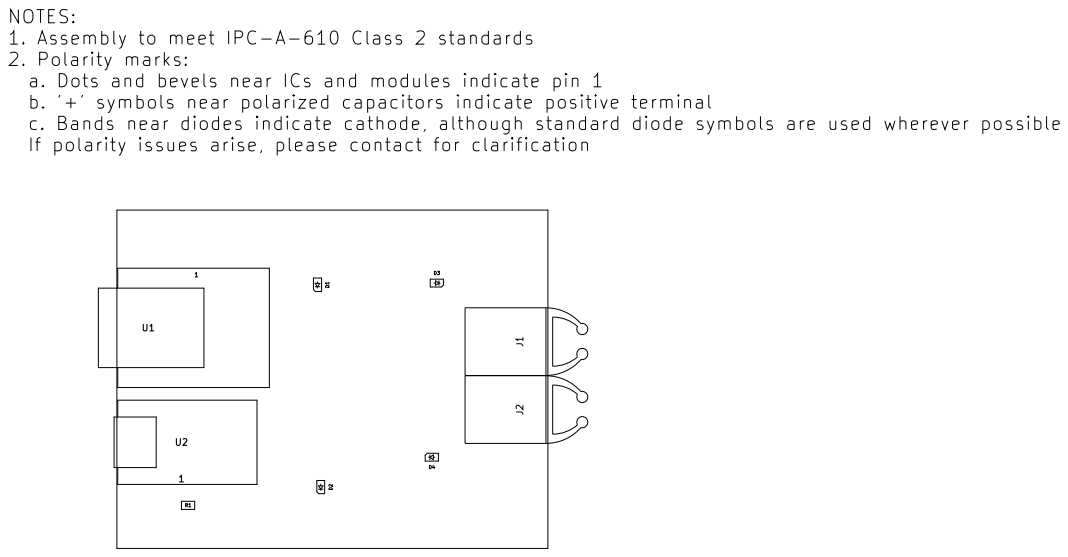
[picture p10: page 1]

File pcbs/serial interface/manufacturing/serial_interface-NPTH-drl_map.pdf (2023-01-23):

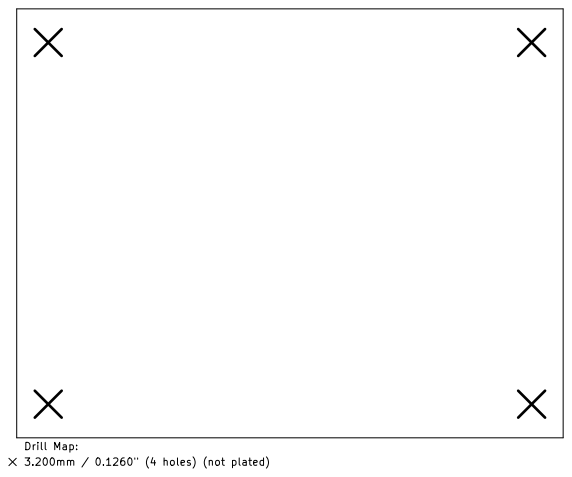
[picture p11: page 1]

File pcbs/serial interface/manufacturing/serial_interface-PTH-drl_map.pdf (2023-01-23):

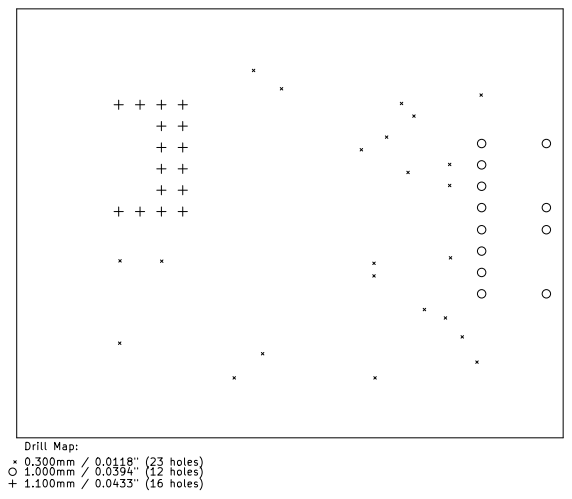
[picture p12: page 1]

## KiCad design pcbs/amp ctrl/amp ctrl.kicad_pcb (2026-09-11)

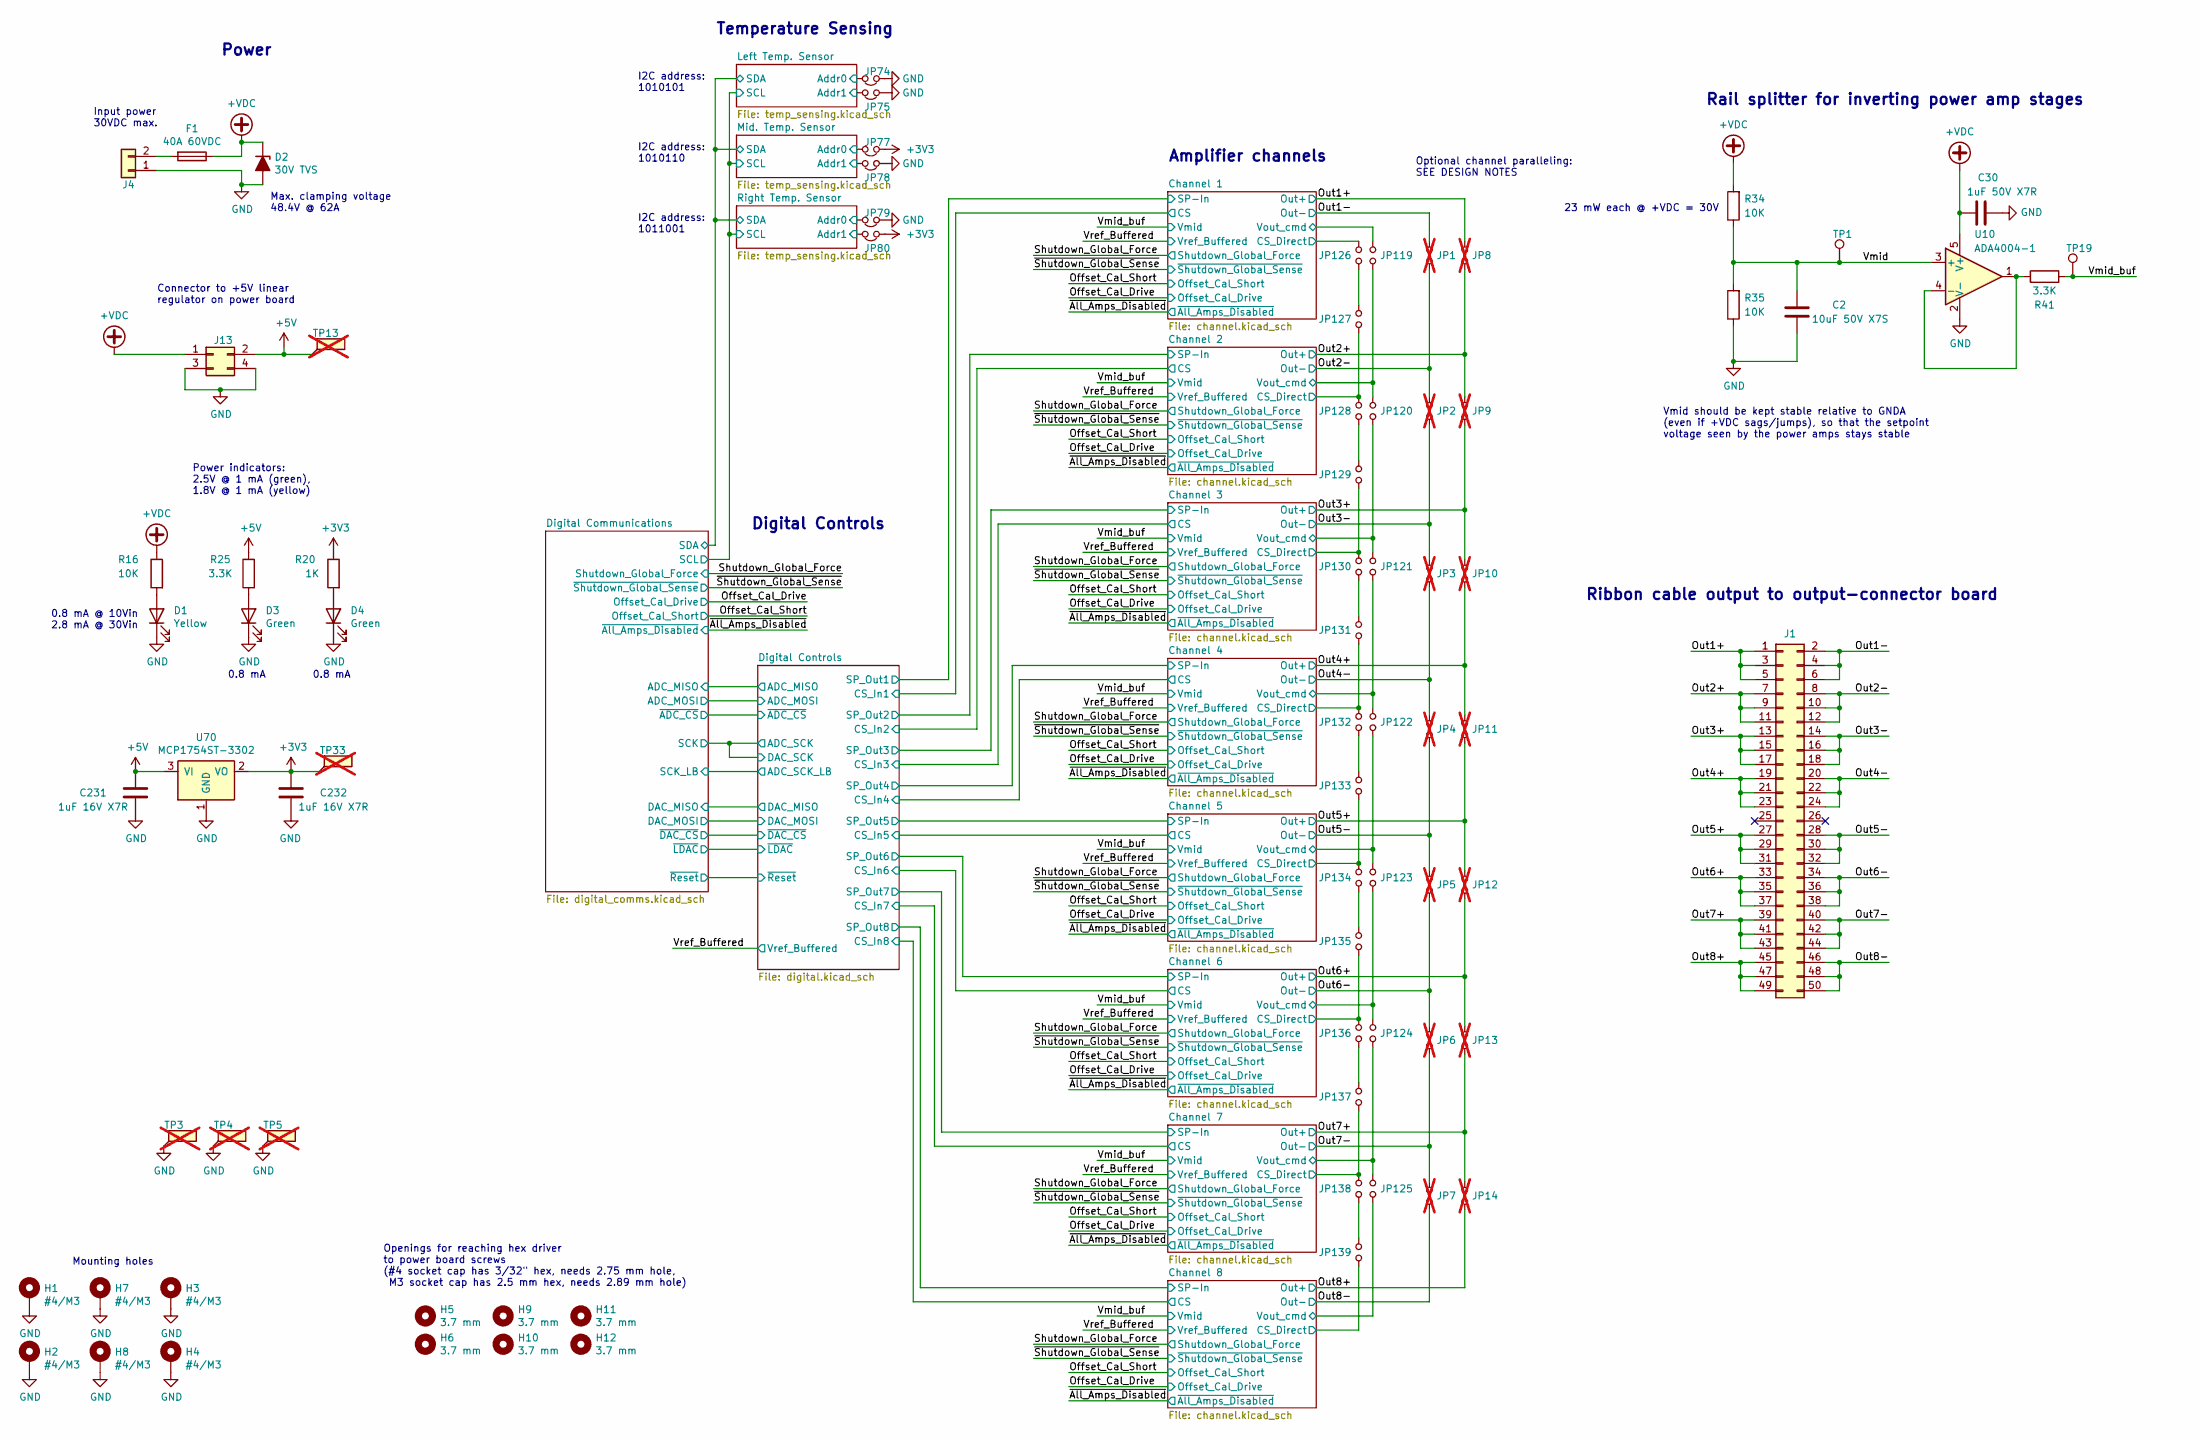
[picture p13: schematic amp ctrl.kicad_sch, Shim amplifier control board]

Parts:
C2: 10uF 50V X7S; C_1210_3225Metric; MPN GCM32EC71H106KA03L
C30: 1uF 50V X7R; C_0805_2012Metric; MPN C0805C105K3RACTU
C231, C232: 1uF 16V X7R; C_0603_1608Metric; MPN C0603C105K4RACTU
D1: Yellow; LED_Kingbright_APA3010_3x2mm_Horizontal; MPN APA3010SYCK-GX
D2: 30V TVS; D_SMC; MPN SMDJ30A
D3, D4: Green; LED_Kingbright_APA3010_3x2mm_Horizontal; MPN APA3010ZGC-GX
F1: 40A 60VDC; Fuse_12.4x4.5mm_SMT; MPN 0456040.DR
H1, H2, H3, H4, H7, H8: #4/M3; MountingHole_3.2mm_M3_Pad_Via
H5, H6, H9, H10, H11, H12: 3.7 mm; MountingHole_3.7mm
J1: Conn_02x25_Odd_Even; PinHeader_2x25_P2.54mm_Vertical_Shrouded; MPN SBH11-PBPC-D25-ST-BK
J4: Conn_01x02; Connector_Phoenix_1190363; MPN 1190363
J13: Conn_02x02; PinSocket_2x02_P2.54mm_Vertical_SMD_BotEntry_Pin; MPN M20-7810245 / M20-7810245R
JP1, JP2, JP3, JP4, JP5, JP6, JP7, JP8, JP9, JP10, JP11, JP12, JP13, JP14: Jumper_NO_Small; Jumper_SMT_Gap-3mm; MPN 5100TR; not fitted
JP74, JP75, JP77, JP78, JP79, JP80: Jumper_NC_Small; SolderJumper-2_P1.3mm_Bridged_RoundedPad1.0x1.5mm
JP119, JP120, JP121, JP122, JP123, JP124, JP125, JP126, JP127, JP128, JP129, JP130, JP131, JP132, JP133, JP134, JP135, JP136, JP137, JP138, JP139: Jumper_NO_Small; SolderJumper-2_P1.3mm_Open_TrianglePad1.0x1.5mm
R16, R34, R35: 10K; R_0805_2012Metric; MPN RK73H2ATTD1002F
R20: 1K; R_0805_2012Metric; MPN RK73H2ATTD1001F
R25, R41: 3.3K; R_0805_2012Metric; MPN RK73H2ATTD3301F
TP1, TP19: TestPoint; TestPoint_Pad_D1.5mm
TP3, TP4, TP5, TP13, TP33: TestPoint_Flag; TestPoint_Keystone_5019_Miniature; MPN 5019; not fitted
U10: ADA4004-1; SOT-23-5; MPN ADA4004-1ARJZ-R7
U70: MCP1754ST-3302; SOT-23; MPN MCP1754ST-3302E/CB

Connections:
+3V3: C232.1, JP77.1, JP80.1, R20.1, TP33.1 (1_1), U70.2 (VO); also elsewhere on the board
+5V: C231.1, J13.2, R25.1, TP13.1 (1_1), U70.3 (VI); also elsewhere on the board
+VDC: C30.2, D2.1 (K), F1.1, J13.1, R16.1, R34.2, U10.5 (V+); also elsewhere on the board
/Channel 1/CS_Direct: JP126.2; also elsewhere on the board
/Channel 1/Vout_cmd: JP119.2; also elsewhere on the board
/Channel 2/CS_Direct: JP127.1, JP128.2; also elsewhere on the board
/Channel 2/Vout_cmd: JP119.1, JP120.2; also elsewhere on the board
/Channel 3/CS_Direct: JP129.1, JP130.2; also elsewhere on the board
/Channel 3/Vout_cmd: JP120.1, JP121.2; also elsewhere on the board
/Channel 4/CS_Direct: JP131.1, JP132.2; also elsewhere on the board
/Channel 4/Vout_cmd: JP121.1, JP122.2; also elsewhere on the board
/Channel 5/CS_Direct: JP133.1, JP134.2; also elsewhere on the board
/Channel 5/Vout_cmd: JP122.1, JP123.2; also elsewhere on the board
/Channel 6/CS_Direct: JP135.1, JP136.2; also elsewhere on the board
/Channel 6/Vout_cmd: JP123.1, JP124.2; also elsewhere on the board
/Channel 7/CS_Direct: JP137.1, JP138.2; also elsewhere on the board
/Channel 7/Vout_cmd: JP124.1, JP125.2; also elsewhere on the board
/Channel 8/CS_Direct: JP139.1; also elsewhere on the board
/Channel 8/Vout_cmd: JP125.1; also elsewhere on the board
/Left Temp. Sensor/Addr0: JP74.2; also elsewhere on the board
/Left Temp. Sensor/Addr1: JP75.2; also elsewhere on the board
/Mid. Temp. Sensor/Addr0: JP77.2; also elsewhere on the board
/Mid. Temp. Sensor/Addr1: JP78.2; also elsewhere on the board
/Out1+: J1.1, J1.3, J1.5, JP8.2; also elsewhere on the board
/Out1-: J1.2, J1.4, J1.6, JP1.2; also elsewhere on the board
/Out2+: J1.7, J1.9, J1.11, JP8.1, JP9.2; also elsewhere on the board
/Out2-: J1.8, J1.10, J1.12, JP1.1, JP2.2; also elsewhere on the board
/Out3+: J1.13, J1.15, J1.17, JP9.1, JP10.2; also elsewhere on the board
/Out3-: J1.14, J1.16, J1.18, JP2.1, JP3.2; also elsewhere on the board
/Out4+: J1.19, J1.21, J1.23, JP10.1, JP11.2; also elsewhere on the board
/Out4-: J1.20, J1.22, J1.24, JP3.1, JP4.2; also elsewhere on the board
/Out5+: J1.27, J1.29, J1.31, JP11.1, JP12.2; also elsewhere on the board
/Out5-: J1.28, J1.30, J1.32, JP4.1, JP5.2; also elsewhere on the board
/Out6+: J1.33, J1.35, J1.37, JP12.1, JP13.2; also elsewhere on the board
/Out6-: J1.34, J1.36, J1.38, JP5.1, JP6.2; also elsewhere on the board
/Out7+: J1.39, J1.41, J1.43, JP13.1, JP14.2; also elsewhere on the board
/Out7-: J1.40, J1.42, J1.44, JP6.1, JP7.2; also elsewhere on the board
/Out8+: J1.45, J1.47, J1.49, JP14.1; also elsewhere on the board
/Out8-: J1.46, J1.48, J1.50, JP7.1; also elsewhere on the board
/Right Temp. Sensor/Addr0: JP79.2; also elsewhere on the board
/Right Temp. Sensor/Addr1: JP80.2; also elsewhere on the board
/Vmid: C2.2, R34.1, R35.2, TP1.1 (1_1), U10.3 (+)
/Vmid_buf: R41.2, TP19.1 (1_1); also elsewhere on the board
GND: C2.1, C30.1, C231.2, C232.2, D1.1 (K), D2.2 (A), D3.1 (K), D4.1 (K), H1.1 (1_1), H2.1 (1_1), H3.1 (1_1), H4.1 (1_1), H7.1 (1_1), H8.1 (1_1), J4.1, J13.3, J13.4, JP74.1, JP75.1, JP78.1, JP79.1, R35.1, TP3.1 (1_1), TP4.1 (1_1), TP5.1 (1_1), U10.2 (V-), U70.1 (GND); also elsewhere on the board
unnamed: D1.2 (A), R16.2
unnamed: D3.2 (A), R25.2
unnamed: D4.2 (A), R20.2
unnamed: F1.2, J4.2
unnamed: JP126.1, JP127.2
unnamed: JP128.1, JP129.2
unnamed: JP130.1, JP131.2
unnamed: JP132.1, JP133.2
unnamed: JP134.1, JP135.2
unnamed: JP136.1, JP137.2
unnamed: JP138.1, JP139.2
unnamed: R41.1, U10.1, U10.4 (-)

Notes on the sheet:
Mounting holes
0.8 mA @ 10Vin 2.8 mA @ 30Vin
Input power 30VDC max.
Openings for reaching hex driver to power board screws (#4 socket cap has 3/32" hex, needs 2.75 mm hole, M3 socket cap has 2.5 mm hex, needs 2.89 mm hole)
Ribbon cable output to output-connector board
Optional channel paralleling: SEE DESIGN NOTES
Temperature Sensing
Power indicators: 2.5V @ 1 mA (green), 1.8V @ 1 mA (yellow)
Amplifier channels
Connector to +5V linear regulator on power board
I2C address: 1011001
I2C address: 1010101
Rail splitter for inverting power amp stages
Power
Vmid should be kept stable relative to GNDA (even if +VDC sags/jumps), so that the setpoint voltage seen by the power amps stays stable
Max. clamping voltage 48.4V @ 62A
Digital Controls
0.8 mA
I2C address: 1010110
23 mW each @ +VDC = 30V

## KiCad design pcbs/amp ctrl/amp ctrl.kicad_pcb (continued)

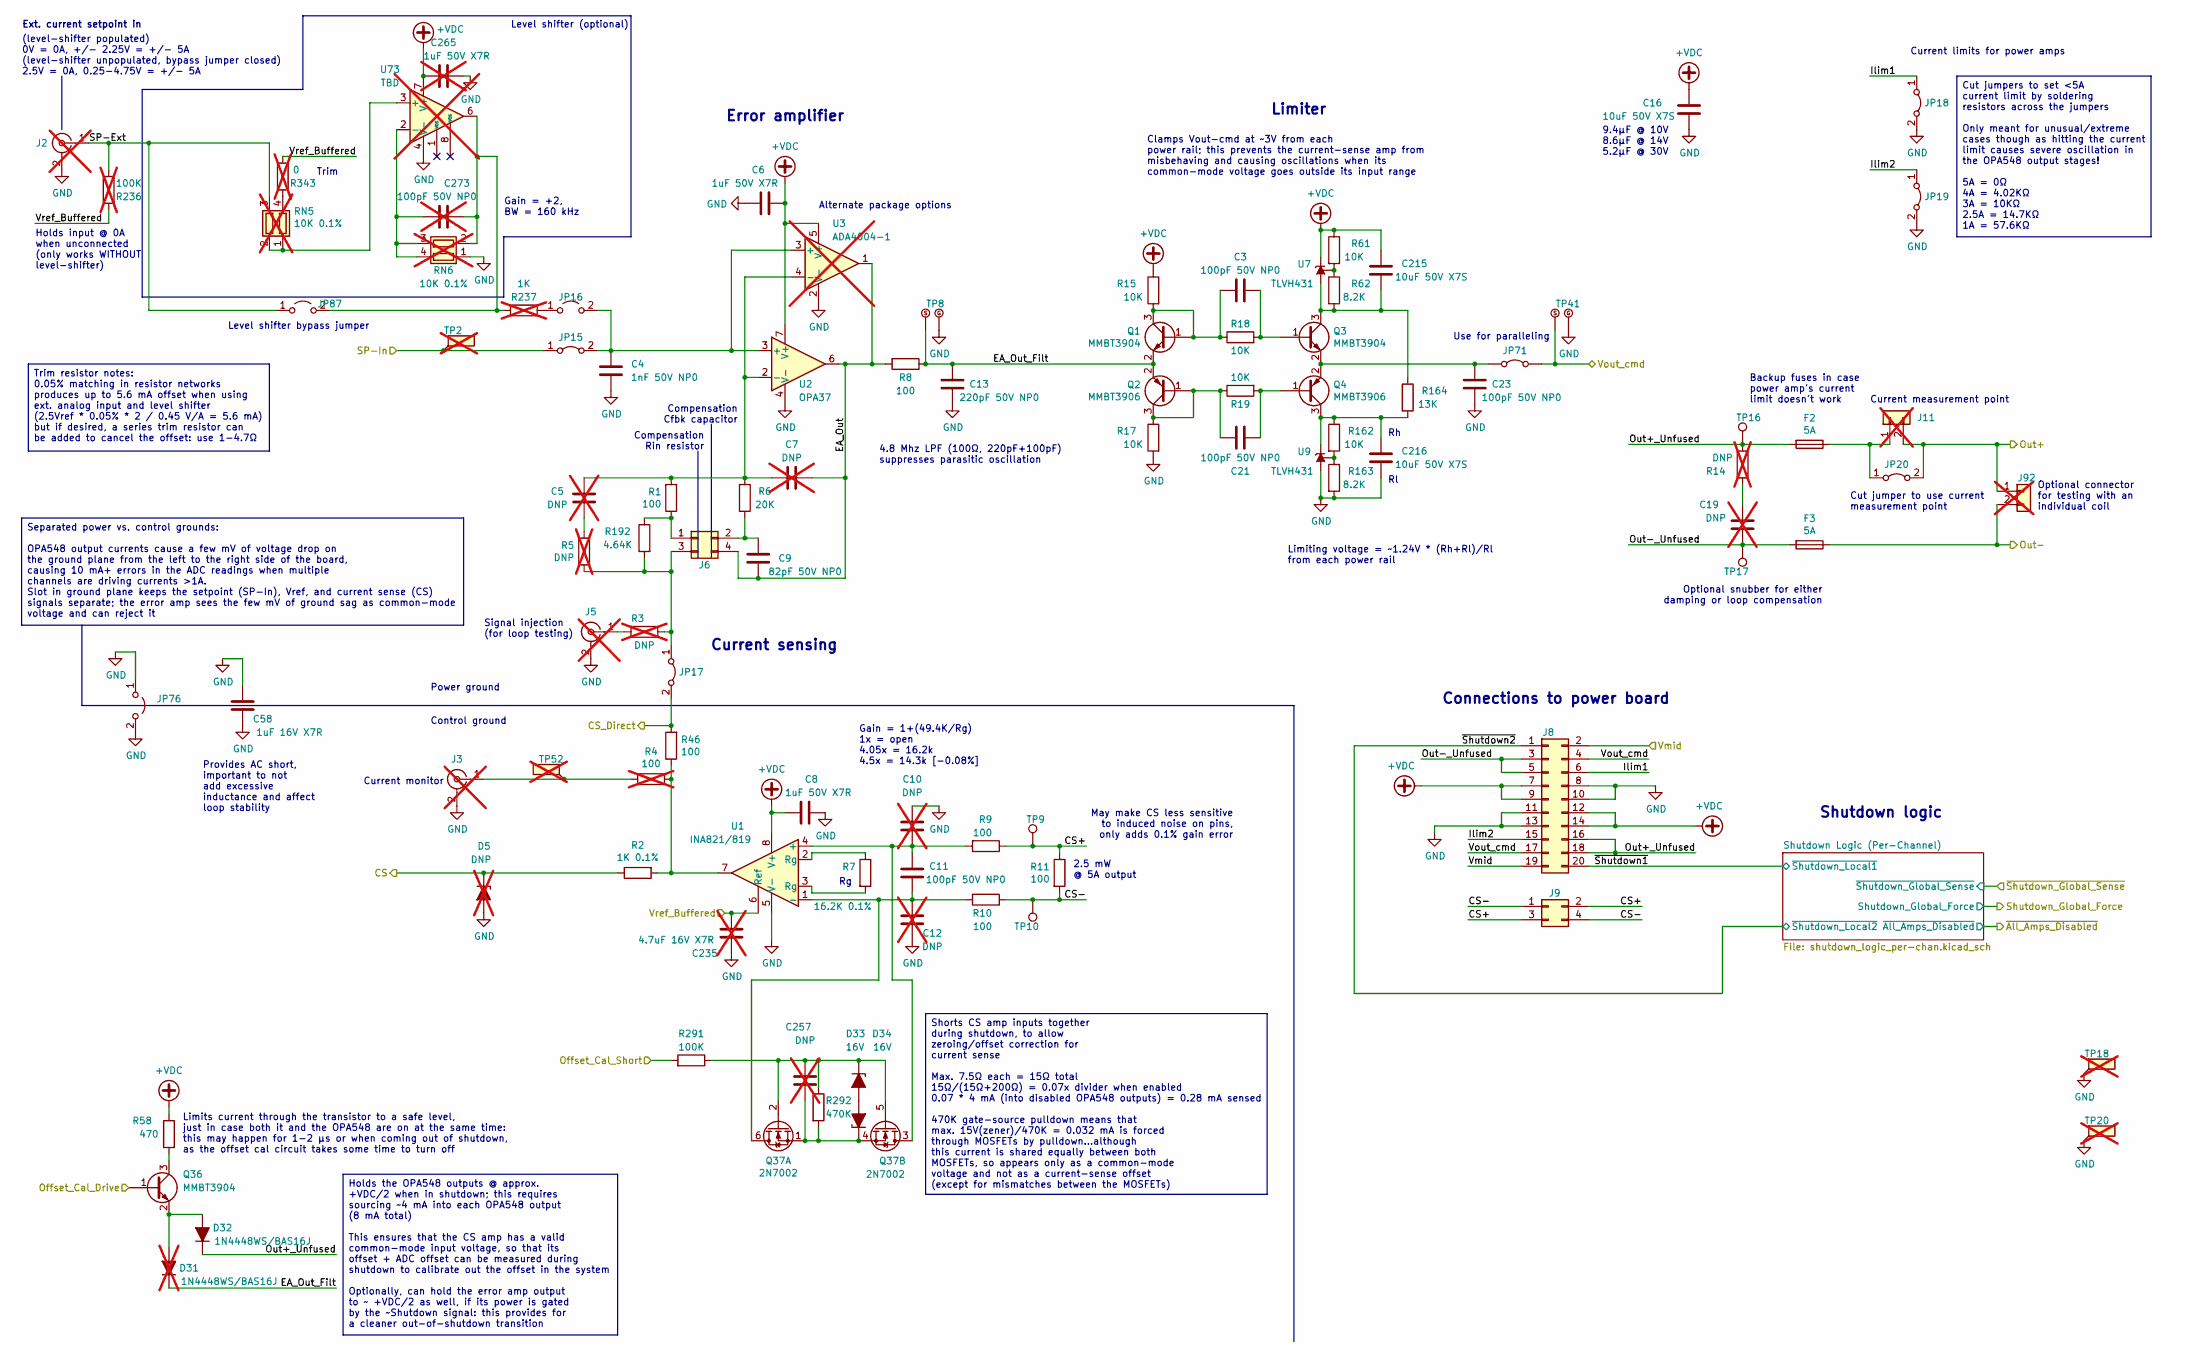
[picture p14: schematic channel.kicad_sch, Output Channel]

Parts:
C3, C11, C21, C23: 100pF 50V NP0; C_0603_1608Metric; MPN C0603C101J5GACTU
C4: 1nF 50V NP0; C_0603_1608Metric; MPN C0603C102J5GACTU
C5, C7, C10, C12: DNP; C_0603_1608Metric; not fitted
C6, C8: 1uF 50V X7R; C_0805_2012Metric; MPN C0805C105K3RACTU
C9: 82pF 50V NP0; C_0603_1608Metric; MPN C0603C820J5GACTU
C13: 220pF 50V NP0; C_0603_1608Metric; MPN C0603C221J5GACTU
C16, C215, C216: 10uF 50V X7S; C_1210_3225Metric; MPN GCM32EC71H106KA03L
C19: DNP; C_1210_3225Metric; not fitted
C58: 1uF 16V X7R; C_0603_1608Metric; MPN C0603C105K4RACTU
C235: 4.7uF 16V X7R; C_0805_2012Metric; MPN C0805C475K4RACTU; not fitted
C257: DNP; C_0603_1608Metric; MPN C0603C101J5GACTU; not fitted
C265: 1uF 50V X7R; C_0805_2012Metric; MPN C0805C105K3RACTU; not fitted
C273: 100pF 50V NP0; C_0603_1608Metric; not fitted
D5: DNP; D_SOD-123; MPN BZT52C6V2-7-F; not fitted
D31: 1N4448WS/BAS16J; D_SOD-323F; MPN BAS16J,115 / BAS16J,135; not fitted
D32: 1N4448WS/BAS16J; D_SOD-323F; MPN BAS16J,115 / BAS16J,135
D33, D34: 16V; D_SOD-323F; MPN UDZVTE-1716B
F2, F3: 5A; Fuse_1206_3216Metric; MPN 3413.0223.22
J2, J3, J5: SMA_Amphenol_132134_Vertical; MPN 132134; not fitted
J6, J9: Conn_02x02; PinSocket_2x02_P2.54mm_Vertical_SMD_BotEntry_Pin; MPN M20-7810245 / M20-7810245R
J8: Conn_02x10_Odd_Even; PinSocket_2x10_P2.54mm_Vertical_SMD_BotEntry_Pin; MPN M20-7811045 / M20-7811045R
J11: Conn_01x02; PinHeader_1x02_P2.54mm_Vertical; not fitted
J92: Conn_01x02; Molex_Mini-Fit_Jr_5566-02A_2x01_P4.20mm_Vertical; MPN 39281023; not fitted
JP15, JP17, JP18, JP19, JP20: Jumper_2_Open; SolderJumper-2_P1.3mm_Bridged_RoundedPad1.0x1.5mm
JP16, JP76, JP87: Jumper_2_Open; SolderJumper-2_P1.3mm_Open_TrianglePad1.0x1.5mm
JP71: Jumper_2_Bridged; SolderJumper-2_P1.3mm_Bridged_RoundedPad1.0x1.5mm
Q1, Q3, Q36: MMBT3904; SOT-23; MPN MMBT3904-7-F
Q2, Q4: MMBT3906; SOT-23; MPN MMBT3906-7-F
Q37: 2N7002; SOT-563; MPN 2N7002VC-7
R1, R8, R9, R10, R11, R46: 100; R_0805_2012Metric; MPN RK73H2ATTD1000F
R2: 1K 0.1%; R_0805_2012Metric; MPN MCU08050D1001BP500
R3, R5, R14: DNP; R_0805_2012Metric; not fitted
R4: 100; R_0805_2012Metric; MPN RK73H2ATTD1000F; not fitted
R6: 20K; R_0805_2012Metric; MPN RK73H2ATTE2002F
R7: 16.2K 0.1%; R_0805_2012Metric; MPN TNPW080516K2BEEA
R15, R17, R18, R19, R61, R162: 10K; R_0805_2012Metric; MPN RK73H2ATTD1002F
R58: 470; R_0805_2012Metric; MPN RK73H2ATTD4700F
R62, R163: 8.2K; R_0805_2012Metric; MPN RK73H2ATTD8201F
R164: 13K; R_0805_2012Metric; MPN RK73H2ATTD1302F
R192: 4.64K; R_0805_2012Metric; MPN RK73H2ATTD4641F
R236: 100K; R_0805_2012Metric; not fitted
R237: 1K; R_0805_2012Metric; not fitted
R291: 100K; R_0805_2012Metric; MPN RK73H2ATTD1003F
R292: 470K; R_0805_2012Metric; MPN RK73H2ATTD4703F
R343: 0; R_0805_2012Metric; not fitted
RN5, RN6: 10K 0.1%; R_Array_Convex_2x0606; MPN ACASN1002S1002P1AT; not fitted
TP2, TP18, TP20, TP52: TestPoint_Flag; TestPoint_Keystone_5019_Miniature; MPN 5019; not fitted
TP8, TP41: TestPoint_2Pole_Vert; TestPoint_2Pads_Pitch4mm_Drill1mm0.7mm
TP9, TP10, TP16, TP17: TestPoint; TestPoint_Pad_D1.5mm
U1: INA821/819; SOIC-8_3.9x4.9mm_P1.27mm; MPN INA821ID
U2: OPA37; SOIC-8_3.9x4.9mm_P1.27mm; MPN OPA37GU/2K5
U3: ADA4004-1; SOT-23-5; not fitted
U7, U9: TLVH431; SOT-23; MPN TLVH431IDBZR
U73: TBD; SOIC-8_3.9x4.9mm_P1.27mm; not fitted

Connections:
+VDC: C6.2, C8.1, C16.2, C215.2, C265.1, J8.7, J8.9, J8.12, J8.14, R15.1, R58.1, R61.1, U1.8 (V+), U2.7 (V+), U3.5 (V+), U7.2 (K), U73.7 (V+); also elsewhere on the board
/Channel 1/CS: D5.1 (K), R2.1; also elsewhere on the board
/Channel 1/CS+: J9.2, J9.3, R9.1, R11.1, TP9.1 (1_1)
/Channel 1/CS-: J9.1, J9.4, R10.1, R11.2, TP10.1 (1_1)
/Channel 1/CS_Direct: JP17.2 (B), R46.2; also elsewhere on the board
/Channel 1/EA_Out: C7.1, C9.1, J6.4, R8.2, U2.6, U3.1
/Channel 1/EA_Out_Filt: C13.2, D31.1 (K), Q1.2 (E), Q2.2 (E), R8.1, TP8.1 (S)
/Channel 1/Ilim1: J8.6, JP18.1 (A)
/Channel 1/Ilim2: J8.15, JP19.1 (A)
/Channel 1/Out+_Unfused: D32.1 (K), F2.2, J8.16, J8.18, R14.2, TP16.1 (1_1)
/Channel 1/Out-_Unfused: C19.2, F3.2, J8.3, J8.5, TP17.1 (1_1)
/Channel 1/SP-Ext: J2.1 (In), JP87.1 (A), R236.1, RN5.3 (R2.2)
/Channel 1/Vout_cmd: J8.4, J8.17, JP71.2 (B), TP41.1 (S); also elsewhere on the board
/Channel 1/~Shutdown1: J8.20; also elsewhere on the board
/Channel 1/~Shutdown2: J8.1; also elsewhere on the board
/Digital Controls/Filter1B: JP15.1 (A), TP2.1 (1_1); also elsewhere on the board
/Offset_Cal_Drive: Q36.1 (B); also elsewhere on the board
/Offset_Cal_Short: R291.2; also elsewhere on the board
/Out1+: J11.2, J92.1, JP20.2 (B); also elsewhere on the board
/Out1-: F3.1, J92.2; also elsewhere on the board
/Vmid_buf: J8.2, J8.19; also elsewhere on the board
/Vref_Buffered: C235.1, R236.2, R343.1, U1.6 (Ref); also elsewhere on the board
GND: C4.2, C6.1, C8.2, C10.1, C12.2, C13.1, C16.1, C23.1, C58.1, C58.2, C216.1, C235.2, C265.2, D5.2 (A), J2.2 (Ext), J3.2 (Ext), J5.2 (Ext), J8.8, J8.10, J8.11, J8.13, JP18.2 (B), JP19.2 (B), JP76.1 (A), JP76.2 (B), R17.2, R163.2, RN6.1 (R1.1), TP8.2 (G), TP18.1 (1_1), TP20.1 (1_1), TP41.2 (G), U1.5 (V-), U2.4 (V-), U3.2 (V-), U9.3 (A), U73.4 (V-); also elsewhere on the board
unnamed: C5.2, R5.2
unnamed: C19.1, R14.1
unnamed: D31.2 (A), D32.2 (A), Q36.2 (E)
unnamed: D33.2 (A), D34.2 (A)
unnamed: C257.1, D33.1 (K), Q37.2 (G), Q37.5 (G), R291.1, R292.1
unnamed: C257.2, D34.1 (K), Q37.1 (S), Q37.4 (S), R292.2
unnamed: J3.1 (In), R4.1, TP52.1 (1_1)
unnamed: J5.1 (In), R3.2
unnamed: J6.1, R1.1, R192.1
unnamed: C9.2, J6.2, R6.2
unnamed: J6.3, JP17.1 (A), R3.1, R5.1, R192.2
unnamed: F2.1, J11.1, JP20.1 (A)
unnamed: C4.1, JP15.2 (B), JP16.2 (B), U2.3 (+), U3.3 (+)
unnamed: JP16.1 (A), R237.2
unnamed: C23.2, JP71.1 (A), Q3.2 (E), Q4.2 (E)
unnamed: C273.1, JP87.2 (B), R237.1, RN6.2 (R2.1), U73.6
unnamed: C3.1, Q1.1 (B), Q1.3 (C), R15.2, R18.1
unnamed: C21.1, Q2.1 (B), Q2.3 (C), R17.1, R19.1
unnamed: C3.2, Q3.1 (B), R18.2
unnamed: C215.1, Q3.3 (C), R62.2, R164.1, U7.3 (A)
unnamed: C21.2, Q4.1 (B), R19.2
unnamed: C216.2, Q4.3 (C), R162.1, R164.2, U9.2 (K)
unnamed: Q36.3 (C), R58.2
unnamed: C11.2, C12.1, Q37.6 (D), R10.2, U1.1 (-)
unnamed: C10.2, C11.1, Q37.3 (D), R9.2, U1.4 (+)
unnamed: R2.2, R4.2, R46.1, U1.7
unnamed: R7.1, U1.2 (Rg)
unnamed: R7.2, U1.3 (Rg)
unnamed: RN5.1 (R1.1), RN5.2 (R2.1), U73.3 (+)
unnamed: R343.2, RN5.4 (R1.2)
unnamed: C273.2, RN6.3 (R2.2), RN6.4 (R1.2), U73.2 (-)
unnamed: C5.1, C7.2, R1.2, R6.1, U2.2 (-), U3.4 (-)
unnamed: R61.2, R62.1, U7.1 (REF)
unnamed: R162.2, R163.1, U9.1 (REF)

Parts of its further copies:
C60, C61, C62, C63, C64, C243, C281: 1uF 16V X7R; C_0603_1608Metric; MPN C0603C105K4RACTU
C65, C66, C67, C68, C76, C85, C93, C102, C110, C119, C127, C136, C144, C153, C161, C170, C178, C187, C188, C189, C190, C191, C192, C193, C194, C195, C196, C197: 100pF 50V NP0; C_0603_1608Metric; MPN C0603C101J5GACTU
C69, C86, C103, C120, C137, C154, C171: 1nF 50V NP0; C_0603_1608Metric; MPN C0603C102J5GACTU
C70, C72, C75, C77, C87, C89, C92, C94, C104, C106, C109, C111, C121, C123, C126, C128, C138, C140, C143, C145, C155, C157, C160, C162, C172, C174, C177, C179: DNP; C_0603_1608Metric; not fitted
C71, C73, C88, C90, C105, C107, C122, C124, C139, C141, C156, C158, C173, C175: 1uF 50V X7R; C_0805_2012Metric; MPN C0805C105K3RACTU
C74, C91, C108, C125, C142, C159, C176: 82pF 50V NP0; C_0603_1608Metric; MPN C0603C820J5GACTU
C78, C95, C112, C129, C146, C163, C180: 220pF 50V NP0; C_0603_1608Metric; MPN C0603C221J5GACTU
C81, C98, C115, C132, C149, C166, C183, C217, C218, C219, C220, C221, C222, C223, C224, C225, C226, C227, C228, C229, C230: 10uF 50V X7S; C_1210_3225Metric; MPN GCM32EC71H106KA03L
C84, C101, C118, C135, C152, C169, C186: DNP; C_1210_3225Metric; not fitted
C236, C237, C238, C239, C240, C241, C242: 4.7uF 16V X7R; C_0805_2012Metric; MPN C0805C475K4RACTU; not fitted
C258, C259, C260, C261, C262, C263, C264: DNP; C_0603_1608Metric; MPN C0603C101J5GACTU; not fitted
C266, C267, C268, C269, C270, C271, C272: 1uF 50V X7R; C_0805_2012Metric; MPN C0805C105K3RACTU; not fitted
C274, C275, C276, C277, C278, C279, C280: 100pF 50V NP0; C_0603_1608Metric; not fitted
D6, D7, D8, D9, D10, D11, D12: DNP; D_SOD-123; MPN BZT52C6V2-7-F; not fitted
D37, D43, D49, D55, D61, D67, D73: 1N4448WS/BAS16J; D_SOD-323F; MPN BAS16J,115 / BAS16J,135; not fitted
D38, D44, D50, D56, D62, D68, D74: 1N4448WS/BAS16J; D_SOD-323F; MPN BAS16J,115 / BAS16J,135
D39, D40, D45, D46, D51, D52, D57, D58, D63, D64, D69, D70, D75, D76: 16V; D_SOD-323F; MPN UDZVTE-1716B
F4, F5, F6, F7, F8, F9, F10, F11, F12, F13, F14, F15, F16, F17: 5A; Fuse_1206_3216Metric; MPN 3413.0223.22
J21, J24, J31, J34, J41, J44, J51, J54, J61, J64, J71, J74, J81, J84: Conn_02x02; PinSocket_2x02_P2.54mm_Vertical_SMD_BotEntry_Pin; MPN M20-7810245 / M20-7810245R
J23, J33, J43, J53, J63, J73, J83: Conn_02x10_Odd_Even; PinSocket_2x10_P2.54mm_Vertical_SMD_BotEntry_Pin; MPN M20-7811045 / M20-7811045R
J26, J36, J46, J56, J66, J76, J86: Conn_01x02; PinHeader_1x02_P2.54mm_Vertical; not fitted
J93, J94, J95, J96, J97, J98, J99: Conn_01x02; Molex_Mini-Fit_Jr_5566-02A_2x01_P4.20mm_Vertical; MPN 39281023; not fitted
JP22, JP24, JP25, JP26, JP27, JP29, JP31, JP32, JP33, JP34, JP36, JP38, JP39, JP40, JP41, JP43, JP45, JP46, JP47, JP48, JP50, JP52, JP53, JP54, JP55, JP57, JP59, JP60, JP61, JP62, JP64, JP66, JP67, JP68, JP69: Jumper_2_Open; SolderJumper-2_P1.3mm_Bridged_RoundedPad1.0x1.5mm
JP23, JP30, JP37, JP44, JP51, JP58, JP65, JP88, JP89, JP90, JP91, JP92, JP93, JP94, JP95, JP96, JP97, JP98, JP99, JP100, JP101: Jumper_2_Open; SolderJumper-2_P1.3mm_Open_TrianglePad1.0x1.5mm
JP112, JP113, JP114, JP115, JP116, JP117, JP118: Jumper_2_Bridged; SolderJumper-2_P1.3mm_Bridged_RoundedPad1.0x1.5mm
Q5, Q7, Q9, Q11, Q13, Q15, Q17, Q19, Q21, Q23, Q25, Q27, Q29, Q31, Q40, Q44, Q48, Q52, Q56, Q60, Q64: MMBT3904; SOT-23; MPN MMBT3904-7-F
Q6, Q8, Q10, Q12, Q14, Q16, Q18, Q20, Q22, Q24, Q26, Q28, Q30, Q32: MMBT3906; SOT-23; MPN MMBT3906-7-F
Q41, Q45, Q49, Q53, Q57, Q61, Q65: 2N7002; SOT-563; MPN 2N7002VC-7
R47, R48, R49, R50, R51, R52, R64, R71, R72, R73, R74, R78, R85, R86, R87, R88, R92, R99, R100, R101, R102, R106, R113, R114, R115, R116, R120, R127, R128, R129, R130, R134, R141, R142, R143, R144, R148, R155, R156, R157, R158, R294: 100; R_0805_2012Metric; MPN RK73H2ATTD1000F
R65, R79, R93, R107, R121, R135, R149: 1K 0.1%; R_0805_2012Metric; MPN MCU08050D1001BP500
R66, R68, R77, R80, R82, R91, R94, R96, R105, R108, R110, R119, R122, R124, R133, R136, R138, R147, R150, R152, R161: DNP; R_0805_2012Metric; not fitted
R67, R81, R95, R109, R123, R137, R151: 100; R_0805_2012Metric; MPN RK73H2ATTD1000F; not fitted
R69, R83, R97, R111, R125, R139, R153: 20K; R_0805_2012Metric; MPN RK73H2ATTE2002F
R70, R84, R98, R112, R126, R140, R154: 16.2K 0.1%; R_0805_2012Metric; MPN TNPW080516K2BEEA
R167, R168, R169, R170, R171, R172, R182: 470; R_0805_2012Metric; MPN RK73H2ATTD4700F
R183, R184, R185, R186, R187, R189, R194, R195, R196, R197, R198, R200, R205, R206, R207, R208, R209, R211, R216, R217, R218, R219, R220, R222, R227, R228, R229, R230, R231, R233, R238, R239, R240, R241, R242, R244, R249, R250, R251, R252, R253, R255: 10K; R_0805_2012Metric; MPN RK73H2ATTD1002F
R188, R190, R199, R201, R210, R212, R221, R223, R232, R234, R243, R245, R254, R256: 8.2K; R_0805_2012Metric; MPN RK73H2ATTD8201F
R191, R202, R213, R224, R235, R246, R257: 13K; R_0805_2012Metric; MPN RK73H2ATTD1302F
R193, R203, R204, R214, R215, R225, R226: 4.64K; R_0805_2012Metric; MPN RK73H2ATTD4641F
R247, R258, R275, R277, R279, R281, R283: 100K; R_0805_2012Metric; not fitted
R248, R259, R276, R278, R280, R282, R284: 1K; R_0805_2012Metric; not fitted
R297, R303, R309, R315, R321, R327, R333: 100K; R_0805_2012Metric; MPN RK73H2ATTD1003F
R298, R304, R310, R316, R322, R328, R334: 470K; R_0805_2012Metric; MPN RK73H2ATTD4703F
R344, R345, R346, R347, R348, R349, R350: 0; R_0805_2012Metric; not fitted
RN7, RN8, RN9, RN10, RN11, RN12, RN13, RN14, RN15, RN16, RN17, RN18, RN19, RN20: 10K 0.1%; R_Array_Convex_2x0606; MPN ACASN1002S1002P1AT; not fitted
TP50, TP51, TP65, TP79, TP93, TP107, TP121, TP135, TP149, TP160, TP161, TP162, TP163, TP164: TestPoint_2Pole_Vert; TestPoint_2Pads_Pitch4mm_Drill1mm0.7mm
TP53, TP54, TP55, TP56, TP57, TP58, TP59, TP62, TP74, TP75, TP76, TP88, TP89, TP90, TP102, TP103, TP104, TP116, TP117, TP118, TP130, TP131, TP132, TP144, TP145, TP146, TP158, TP159: TestPoint_Flag; TestPoint_Keystone_5019_Miniature; MPN 5019; not fitted
TP66, TP67, TP72, TP73, TP80, TP81, TP86, TP87, TP94, TP95, TP100, TP101, TP108, TP109, TP114, TP115, TP122, TP123, TP128, TP129, TP136, TP137, TP142, TP143, TP150, TP151, TP156, TP157: TestPoint; TestPoint_Pad_D1.5mm
U13, U18, U23, U28, U33, U38, U43: INA821/819; SOIC-8_3.9x4.9mm_P1.27mm; MPN INA821ID
U14, U19, U24, U29, U34, U39, U44: OPA37; SOIC-8_3.9x4.9mm_P1.27mm; MPN OPA37GU/2K5
U15, U20, U25, U30, U35, U40, U45: ADA4004-1; SOT-23-5; not fitted
U48, U49, U50, U51, U52, U53, U54, U55, U56, U57, U58, U59, U60, U61: TLVH431; SOT-23; MPN TLVH431IDBZR
U76, U79, U81, U84, U87, U88, U89: TBD; SOIC-8_3.9x4.9mm_P1.27mm; not fitted

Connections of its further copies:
+VDC: C71.2, C73.1, C81.2, C88.2, C90.1, C98.2, C105.2, C107.1, C115.2, C122.2, C124.1, C132.2, C139.2, C141.1, C149.2, C156.2, C158.1, C166.2, C173.2, C175.1, C183.2, C217.2, C219.2, C221.2, C223.2, C225.2, C227.2, C229.2, C266.1, C267.1, C268.1, C269.1, C270.1, C271.1, C272.1, J23.7, J23.9, J23.12, J23.14, J33.7, J33.9, J33.12, J33.14, J43.7, J43.9, J43.12, J43.14, J53.7, J53.9, J53.12, J53.14, J63.7, J63.9, J63.12, J63.14, J73.7, J73.9, J73.12, J73.14, J83.7, J83.9, J83.12, J83.14, R167.1, R168.1, R169.1, R170.1, R171.1, R172.1, R182.1, R183.1, R187.1, R194.1, R198.1, R205.1, R209.1, R216.1, R220.1, R227.1, R231.1, R238.1, R242.1, R249.1, R253.1, U13.8 (V+), U14.7 (V+), U15.5 (V+), U18.8 (V+), U19.7 (V+), U20.5 (V+), U23.8 (V+), U24.7 (V+), U25.5 (V+), U28.8 (V+), U29.7 (V+), U30.5 (V+), U33.8 (V+), U34.7 (V+), U35.5 (V+), U38.8 (V+), U39.7 (V+), U40.5 (V+), U43.8 (V+), U44.7 (V+), U45.5 (V+), U48.2 (K), U50.2 (K), U52.2 (K), U54.2 (K), U56.2 (K), U58.2 (K), U60.2 (K), U76.7 (V+), U79.7 (V+), U81.7 (V+), U84.7 (V+), U87.7 (V+), U88.7 (V+), U89.7 (V+); also elsewhere on the board
/Channel 2/CS: D6.1 (K), R65.1; also elsewhere on the board
/Channel 2/CS+: J24.2, J24.3, R72.1, R74.1, TP66.1 (1_1)
/Channel 2/CS-: J24.1, J24.4, R73.1, R74.2, TP67.1 (1_1)
/Channel 2/CS_Direct: JP24.2 (B), R47.2; also elsewhere on the board
/Channel 2/EA_Out: C72.1, C74.1, J21.4, R71.2, U14.6, U15.1
/Channel 2/EA_Out_Filt: C78.2, D37.1 (K), Q5.2 (E), Q6.2 (E), R71.1, TP65.1 (S)
/Channel 2/Ilim1: J23.6, JP25.1 (A)
/Channel 2/Ilim2: J23.15, JP26.1 (A)
/Channel 2/Out+_Unfused: D38.1 (K), F4.2, J23.16, J23.18, R77.2, TP72.1 (1_1)
/Channel 2/Out-_Unfused: C84.2, F5.2, J23.3, J23.5, TP73.1 (1_1)
/Channel 2/SP-Ext: JP88.1 (A), R247.1, RN7.3 (R2.2); also elsewhere on the board
/Channel 2/Vout_cmd: J23.4, J23.17, JP112.2 (B), TP50.1 (S); also elsewhere on the board
/Channel 2/~Shutdown1: J23.20; also elsewhere on the board
/Channel 2/~Shutdown2: J23.1; also elsewhere on the board
/Channel 3/CS: D7.1 (K), R79.1; also elsewhere on the board
/Channel 3/CS+: J34.2, J34.3, R86.1, R88.1, TP80.1 (1_1)
/Channel 3/CS-: J34.1, J34.4, R87.1, R88.2, TP81.1 (1_1)
/Channel 3/CS_Direct: JP31.2 (B), R48.2; also elsewhere on the board
/Channel 3/EA_Out: C89.1, C91.1, J31.4, R85.2, U19.6, U20.1
/Channel 3/EA_Out_Filt: C95.2, D43.1 (K), Q9.2 (E), Q10.2 (E), R85.1, TP79.1 (S)
/Channel 3/Ilim1: J33.6, JP32.1 (A)
/Channel 3/Ilim2: J33.15, JP33.1 (A)
/Channel 3/Out+_Unfused: D44.1 (K), F6.2, J33.16, J33.18, R91.2, TP86.1 (1_1)
/Channel 3/Out-_Unfused: C101.2, F7.2, J33.3, J33.5, TP87.1 (1_1)
/Channel 3/SP-Ext: JP89.1 (A), R258.1, RN9.3 (R2.2); also elsewhere on the board
/Channel 3/Vout_cmd: J33.4, J33.17, JP113.2 (B), TP51.1 (S); also elsewhere on the board
/Channel 3/~Shutdown1: J33.20; also elsewhere on the board
/Channel 3/~Shutdown2: J33.1; also elsewhere on the board
/Channel 4/CS: D8.1 (K), R93.1; also elsewhere on the board
/Channel 4/CS+: J44.2, J44.3, R100.1, R102.1, TP94.1 (1_1)
/Channel 4/CS-: J44.1, J44.4, R101.1, R102.2, TP95.1 (1_1)
/Channel 4/CS_Direct: JP38.2 (B), R49.2; also elsewhere on the board
/Channel 4/EA_Out: C106.1, C108.1, J41.4, R99.2, U24.6, U25.1
/Channel 4/EA_Out_Filt: C112.2, D49.1 (K), Q13.2 (E), Q14.2 (E), R99.1, TP93.1 (S)
/Channel 4/Ilim1: J43.6, JP39.1 (A)
/Channel 4/Ilim2: J43.15, JP40.1 (A)
/Channel 4/Out+_Unfused: D50.1 (K), F8.2, J43.16, J43.18, R105.2, TP100.1 (1_1)
/Channel 4/Out-_Unfused: C118.2, F9.2, J43.3, J43.5, TP101.1 (1_1)
/Channel 4/SP-Ext: JP90.1 (A), R275.1, RN11.3 (R2.2); also elsewhere on the board
/Channel 4/Vout_cmd: J43.4, J43.17, JP114.2 (B), TP160.1 (S); also elsewhere on the board
/Channel 4/~Shutdown1: J43.20; also elsewhere on the board
/Channel 4/~Shutdown2: J43.1; also elsewhere on the board
/Channel 5/CS: D9.1 (K), R107.1; also elsewhere on the board
/Channel 5/CS+: J54.2, J54.3, R114.1, R116.1, TP108.1 (1_1)
/Channel 5/CS-: J54.1, J54.4, R115.1, R116.2, TP109.1 (1_1)
/Channel 5/CS_Direct: JP45.2 (B), R50.2; also elsewhere on the board
/Channel 5/EA_Out: C123.1, C125.1, J51.4, R113.2, U29.6, U30.1
/Channel 5/EA_Out_Filt: C129.2, D55.1 (K), Q17.2 (E), Q18.2 (E), R113.1, TP107.1 (S)
/Channel 5/Ilim1: J53.6, JP46.1 (A)
/Channel 5/Ilim2: J53.15, JP47.1 (A)
/Channel 5/Out+_Unfused: D56.1 (K), F10.2, J53.16, J53.18, R119.2, TP114.1 (1_1)
/Channel 5/Out-_Unfused: C135.2, F11.2, J53.3, J53.5, TP115.1 (1_1)
/Channel 5/SP-Ext: JP91.1 (A), R277.1, RN13.3 (R2.2); also elsewhere on the board
/Channel 5/Vout_cmd: J53.4, J53.17, JP115.2 (B), TP161.1 (S); also elsewhere on the board
/Channel 5/~Shutdown1: J53.20; also elsewhere on the board
/Channel 5/~Shutdown2: J53.1; also elsewhere on the board
/Channel 6/CS: D10.1 (K), R121.1; also elsewhere on the board
/Channel 6/CS+: J64.2, J64.3, R128.1, R130.1, TP122.1 (1_1)
/Channel 6/CS-: J64.1, J64.4, R129.1, R130.2, TP123.1 (1_1)
/Channel 6/CS_Direct: JP52.2 (B), R51.2; also elsewhere on the board
/Channel 6/EA_Out: C140.1, C142.1, J61.4, R127.2, U34.6, U35.1
/Channel 6/EA_Out_Filt: C146.2, D61.1 (K), Q21.2 (E), Q22.2 (E), R127.1, TP121.1 (S)
/Channel 6/Ilim1: J63.6, JP53.1 (A)
/Channel 6/Ilim2: J63.15, JP54.1 (A)
/Channel 6/Out+_Unfused: D62.1 (K), F12.2, J63.16, J63.18, R133.2, TP128.1 (1_1)
/Channel 6/Out-_Unfused: C152.2, F13.2, J63.3, J63.5, TP129.1 (1_1)
/Channel 6/SP-Ext: JP92.1 (A), R279.1, RN15.3 (R2.2); also elsewhere on the board
/Channel 6/Vout_cmd: J63.4, J63.17, JP116.2 (B), TP162.1 (S); also elsewhere on the board
/Channel 6/~Shutdown1: J63.20; also elsewhere on the board
/Channel 6/~Shutdown2: J63.1; also elsewhere on the board
/Channel 7/CS: D11.1 (K), R135.1; also elsewhere on the board
/Channel 7/CS+: J74.2, J74.3, R142.1, R144.1, TP136.1 (1_1)
/Channel 7/CS-: J74.1, J74.4, R143.1, R144.2, TP137.1 (1_1)
/Channel 7/CS_Direct: JP59.2 (B), R52.2; also elsewhere on the board
/Channel 7/EA_Out: C157.1, C159.1, J71.4, R141.2, U39.6, U40.1
/Channel 7/EA_Out_Filt: C163.2, D67.1 (K), Q25.2 (E), Q26.2 (E), R141.1, TP135.1 (S)
/Channel 7/Ilim1: J73.6, JP60.1 (A)
/Channel 7/Ilim2: J73.15, JP61.1 (A)
/Channel 7/Out+_Unfused: D68.1 (K), F14.2, J73.16, J73.18, R147.2, TP142.1 (1_1)
/Channel 7/Out-_Unfused: C169.2, F15.2, J73.3, J73.5, TP143.1 (1_1)
/Channel 7/SP-Ext: JP93.1 (A), R281.1, RN17.3 (R2.2); also elsewhere on the board
/Channel 7/Vout_cmd: J73.4, J73.17, JP117.2 (B), TP163.1 (S); also elsewhere on the board
/Channel 7/~Shutdown1: J73.20; also elsewhere on the board
/Channel 7/~Shutdown2: J73.1; also elsewhere on the board
/Channel 8/CS: D12.1 (K), R149.1; also elsewhere on the board
/Channel 8/CS+: J84.2, J84.3, R156.1, R158.1, TP150.1 (1_1)
/Channel 8/CS-: J84.1, J84.4, R157.1, R158.2, TP151.1 (1_1)
/Channel 8/CS_Direct: JP66.2 (B), R294.2; also elsewhere on the board
/Channel 8/EA_Out: C174.1, C176.1, J81.4, R155.2, U44.6, U45.1
/Channel 8/EA_Out_Filt: C180.2, D73.1 (K), Q29.2 (E), Q30.2 (E), R155.1, TP149.1 (S)
/Channel 8/Ilim1: J83.6, JP67.1 (A)
/Channel 8/Ilim2: J83.15, JP68.1 (A)
/Channel 8/Out+_Unfused: D74.1 (K), F16.2, J83.16, J83.18, R161.2, TP156.1 (1_1)
/Channel 8/Out-_Unfused: C186.2, F17.2, J83.3, J83.5, TP157.1 (1_1)
/Channel 8/SP-Ext: JP94.1 (A), R283.1, RN19.3 (R2.2); also elsewhere on the board
/Channel 8/Vout_cmd: J83.4, J83.17, JP118.2 (B), TP164.1 (S); also elsewhere on the board
/Channel 8/~Shutdown1: J83.20; also elsewhere on the board
/Channel 8/~Shutdown2: J83.1; also elsewhere on the board
/Digital Controls/Filter2B: JP22.1 (A), TP62.1 (1_1); also elsewhere on the board
/Digital Controls/Filter3B: JP29.1 (A), TP76.1 (1_1); also elsewhere on the board
/Digital Controls/Filter4B: JP36.1 (A), TP90.1 (1_1); also elsewhere on the board
/Digital Controls/Filter5B: JP43.1 (A), TP104.1 (1_1); also elsewhere on the board
/Digital Controls/Filter6B: JP50.1 (A), TP118.1 (1_1); also elsewhere on the board
/Digital Controls/Filter7B: JP57.1 (A), TP132.1 (1_1); also elsewhere on the board
/Digital Controls/Filter8B: JP64.1 (A), TP146.1 (1_1); also elsewhere on the board
/Offset_Cal_Drive: Q40.1 (B), Q44.1 (B), Q48.1 (B), Q52.1 (B), Q56.1 (B), Q60.1 (B), Q64.1 (B); also elsewhere on the board
/Offset_Cal_Short: R297.2, R303.2, R309.2, R315.2, R321.2, R327.2, R333.2; also elsewhere on the board
/Out2+: J26.2, J93.1, JP27.2 (B); also elsewhere on the board
/Out2-: F5.1, J93.2; also elsewhere on the board
/Out3+: J36.2, J94.1, JP34.2 (B); also elsewhere on the board
/Out3-: F7.1, J94.2; also elsewhere on the board
/Out4+: J46.2, J95.1, JP41.2 (B); also elsewhere on the board
/Out4-: F9.1, J95.2; also elsewhere on the board
/Out5+: J56.2, J96.1, JP48.2 (B); also elsewhere on the board
/Out5-: F11.1, J96.2; also elsewhere on the board
/Out6+: J66.2, J97.1, JP55.2 (B); also elsewhere on the board
/Out6-: F13.1, J97.2; also elsewhere on the board
/Out7+: J76.2, J98.1, JP62.2 (B); also elsewhere on the board
/Out7-: F15.1, J98.2; also elsewhere on the board
/Out8+: J86.2, J99.1, JP69.2 (B); also elsewhere on the board
/Out8-: F17.1, J99.2; also elsewhere on the board
/Vmid_buf: J23.2, J23.19, J33.2, J33.19, J43.2, J43.19, J53.2, J53.19, J63.2, J63.19, J73.2, J73.19, J83.2, J83.19; also elsewhere on the board
/Vref_Buffered: C236.1, C237.1, C238.1, C239.1, C240.1, C241.1, C242.1, R247.2, R258.2, R275.2, R277.2, R279.2, R281.2, R283.2, R344.1, R345.1, R346.1, R347.1, R348.1, R349.1, R350.1, U13.6 (Ref), U18.6 (Ref), U23.6 (Ref), U28.6 (Ref), U33.6 (Ref), U38.6 (Ref), U43.6 (Ref); also elsewhere on the board
GND: C60.1, C60.2, C61.1, C61.2, C62.1, C62.2, C63.1, C63.2, C64.1, C64.2, C67.1, C69.2, C71.1, C73.2, C75.1, C77.2, C78.1, C81.1, C86.2, C88.1, C90.2, C92.1, C94.2, C95.1, C98.1, C102.1, C103.2, C105.1, C107.2, C109.1, C111.2, C112.1, C115.1, C120.2, C122.1, C124.2, C126.1, C128.2, C129.1, C132.1, C137.2, C139.1, C141.2, C143.1, C145.2, C146.1, C149.1, C153.1, C154.2, C156.1, C158.2, C160.1, C162.2, C163.1, C166.1, C171.2, C173.1, C175.2, C177.1, C179.2, C180.1, C183.1, C188.1, C191.1, C194.1, C197.1, C218.1, C220.1, C222.1, C224.1, C226.1, C228.1, C230.1, C236.2, C237.2, C238.2, C239.2, C240.2, C241.2, C242.2, C243.1, C243.2, C266.2, C267.2, C268.2, C269.2, C270.2, C271.2, C272.2, C281.1, C281.2, D6.2 (A), D7.2 (A), D8.2 (A), D9.2 (A), D10.2 (A), D11.2 (A), D12.2 (A), J23.8, J23.10, J23.11, J23.13, J33.8, J33.10, J33.11, J33.13, J43.8, J43.10, J43.11, J43.13, J53.8, J53.10, J53.11, J53.13, J63.8, J63.10, J63.11, J63.13, J73.8, J73.10, J73.11, J73.13, J83.8, J83.10, J83.11, J83.13, JP25.2 (B), JP26.2 (B), JP32.2 (B), JP33.2 (B), JP39.2 (B), JP40.2 (B), JP46.2 (B), JP47.2 (B), JP53.2 (B), JP54.2 (B), JP60.2 (B), JP61.2 (B), JP67.2 (B), JP68.2 (B), JP95.1 (A), JP95.2 (B), JP96.1 (A), JP96.2 (B), JP97.1 (A), JP97.2 (B), JP98.1 (A), JP98.2 (B), JP99.1 (A), JP99.2 (B), JP100.1 (A), JP100.2 (B), JP101.1 (A), JP101.2 (B), R184.2, R190.2, R195.2, R201.2, R206.2, R212.2, R217.2, R223.2, R228.2, R234.2, R239.2, R245.2, R250.2, R256.2, RN8.1 (R1.1), RN10.1 (R1.1), RN12.1 (R1.1), RN14.1 (R1.1), RN16.1 (R1.1), RN18.1 (R1.1), RN20.1 (R1.1), TP50.2 (G), TP51.2 (G), TP65.2 (G), TP74.1 (1_1), TP75.1 (1_1), TP79.2 (G), TP88.1 (1_1), TP89.1 (1_1), TP93.2 (G), TP102.1 (1_1), TP103.1 (1_1), TP107.2 (G), TP116.1 (1_1), TP117.1 (1_1), TP121.2 (G), TP130.1 (1_1), TP131.1 (1_1), TP135.2 (G), TP144.1 (1_1), TP145.1 (1_1), TP149.2 (G), TP158.1 (1_1), TP159.1 (1_1), TP160.2 (G), TP161.2 (G), TP162.2 (G), TP163.2 (G), TP164.2 (G), U13.5 (V-), U14.4 (V-), U15.2 (V-), U18.5 (V-), U19.4 (V-), U20.2 (V-), U23.5 (V-), U24.4 (V-), U25.2 (V-), U28.5 (V-), U29.4 (V-), U30.2 (V-), U33.5 (V-), U34.4 (V-), U35.2 (V-), U38.5 (V-), U39.4 (V-), U40.2 (V-), U43.5 (V-), U44.4 (V-), U45.2 (V-), U49.3 (A), U51.3 (A), U53.3 (A), U55.3 (A), U57.3 (A), U59.3 (A), U61.3 (A), U76.4 (V-), U79.4 (V-), U81.4 (V-), U84.4 (V-), U87.4 (V-), U88.4 (V-), U89.4 (V-); also elsewhere on the board
unnamed: C70.2, R68.2
unnamed: C84.1, R77.1
unnamed: C87.2, R82.2
unnamed: C101.1, R91.1
unnamed: C104.2, R96.2
unnamed: C118.1, R105.1
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

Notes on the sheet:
Clamps Vout-cmd at ~3V from each power rail; this prevents the current-sense amp from misbehaving and causing oscillations when its common-mode voltage goes outside its input range
Optional connector for testing with an individual coil
Compensation Cfbk capacitor
Limiter
Signal injection (for loop testing)
Current limits for power amps
Current monitor
9.4µF @ 10V 8.6µF @ 14V 5.2µF @ 30V
Power ground
Provides AC short, important to not add excessive inductance and affect loop stability
May make CS less sensitive to induced noise on pins, only adds 0.1% gain error
4.8 Mhz LPF (100Ω, 220pF+100pF) suppresses parasitic oscillation
Optional snubber for either damping or loop compensation
Limits current through the transistor to a safe level, just in case both it and the OPA548 are on at the same time: this may happen for 1-2 µs or when coming out of shutdown, as the offset cal circuit takes some time to turn off
Connections to power board
Gain = 1+(49.4K/Rg) 1x = open 4.05x = 16.2k 4.5x = 14.3k [-0.08%]
Holds input @ 0A when unconnected (only works WITHOUT level-shifter)
Compensation Rin resistor
Level shifter bypass jumper
Alternate package options
Trim
Current measurement point
Limiting voltage = ~1.24V * (Rh+Rl)/Rl from each power rail
Control ground
Cut jumper to use current measurement point
Ext. current setpoint in
(level-shifter populated) 0V = 0A, +/- 2.25V = +/- 5A (level-shifter unpopulated, bypass jumper closed) 2.5V = 0A, 0.25-4.75V = +/- 5A
2.5 mW @ 5A output
Gain = +2, BW = 160 kHz
Level shifter (optional)
Backup fuses in case power amp's current limit doesn't work
Current sensing
Error amplifier
Use for paralleling
Shutdown logic
Shorts CS amp inputs together during shutdown, to allow zeroing/offset correction for current sense Max. 7.5Ω each = 15Ω total 15Ω/(15Ω+200Ω) = 0.07x divider when enabled 0.07 * 4 mA (into disabled OPA548 outputs) = 0.28 mA sensed 470K gate-source pulldown means that max. 15V(zener)/470K = 0.032 mA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
Cut jumpers to set <5A current limit by soldering resistors across the jumpers Only meant for unusual/extreme cases though as hitting the current limit causes severe oscillation in the OPA548 output stages! 5A = 0Ω 4A = 4.02KΩ 3A = 10KΩ 2.5A = 14.7KΩ 1A = 57.6KΩ
Holds the OPA548 outputs @ approx. +VDC/2 when in shutdown; this requires sourcing ~4 mA into each OPA548 output (8 mA total) This ensures that the CS amp has a valid common-mode input voltage, so that its offset + ADC offset can be measured during shutdown to calibrate out the offset in the system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
Trim resistor notes: 0.05% matching in resistor networks produces up to 5.6 mA offset when using ext. analog input and level shifter (2.5Vref * 0.05% * 2 / 0.45 V/A = 5.6 mA) but if desired, a series trim resistor can be added to cancel the offset: use 1-4.7Ω
Separated power vs. control grounds: OPA548 output currents cause a few mV of voltage drop on the ground plane from the left to the right side of the board, causing 10 mA+ errors in the ADC readings when multiple channels are driving currents >1A. Slot in ground plane keeps the setpoint (SP-In), Vr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

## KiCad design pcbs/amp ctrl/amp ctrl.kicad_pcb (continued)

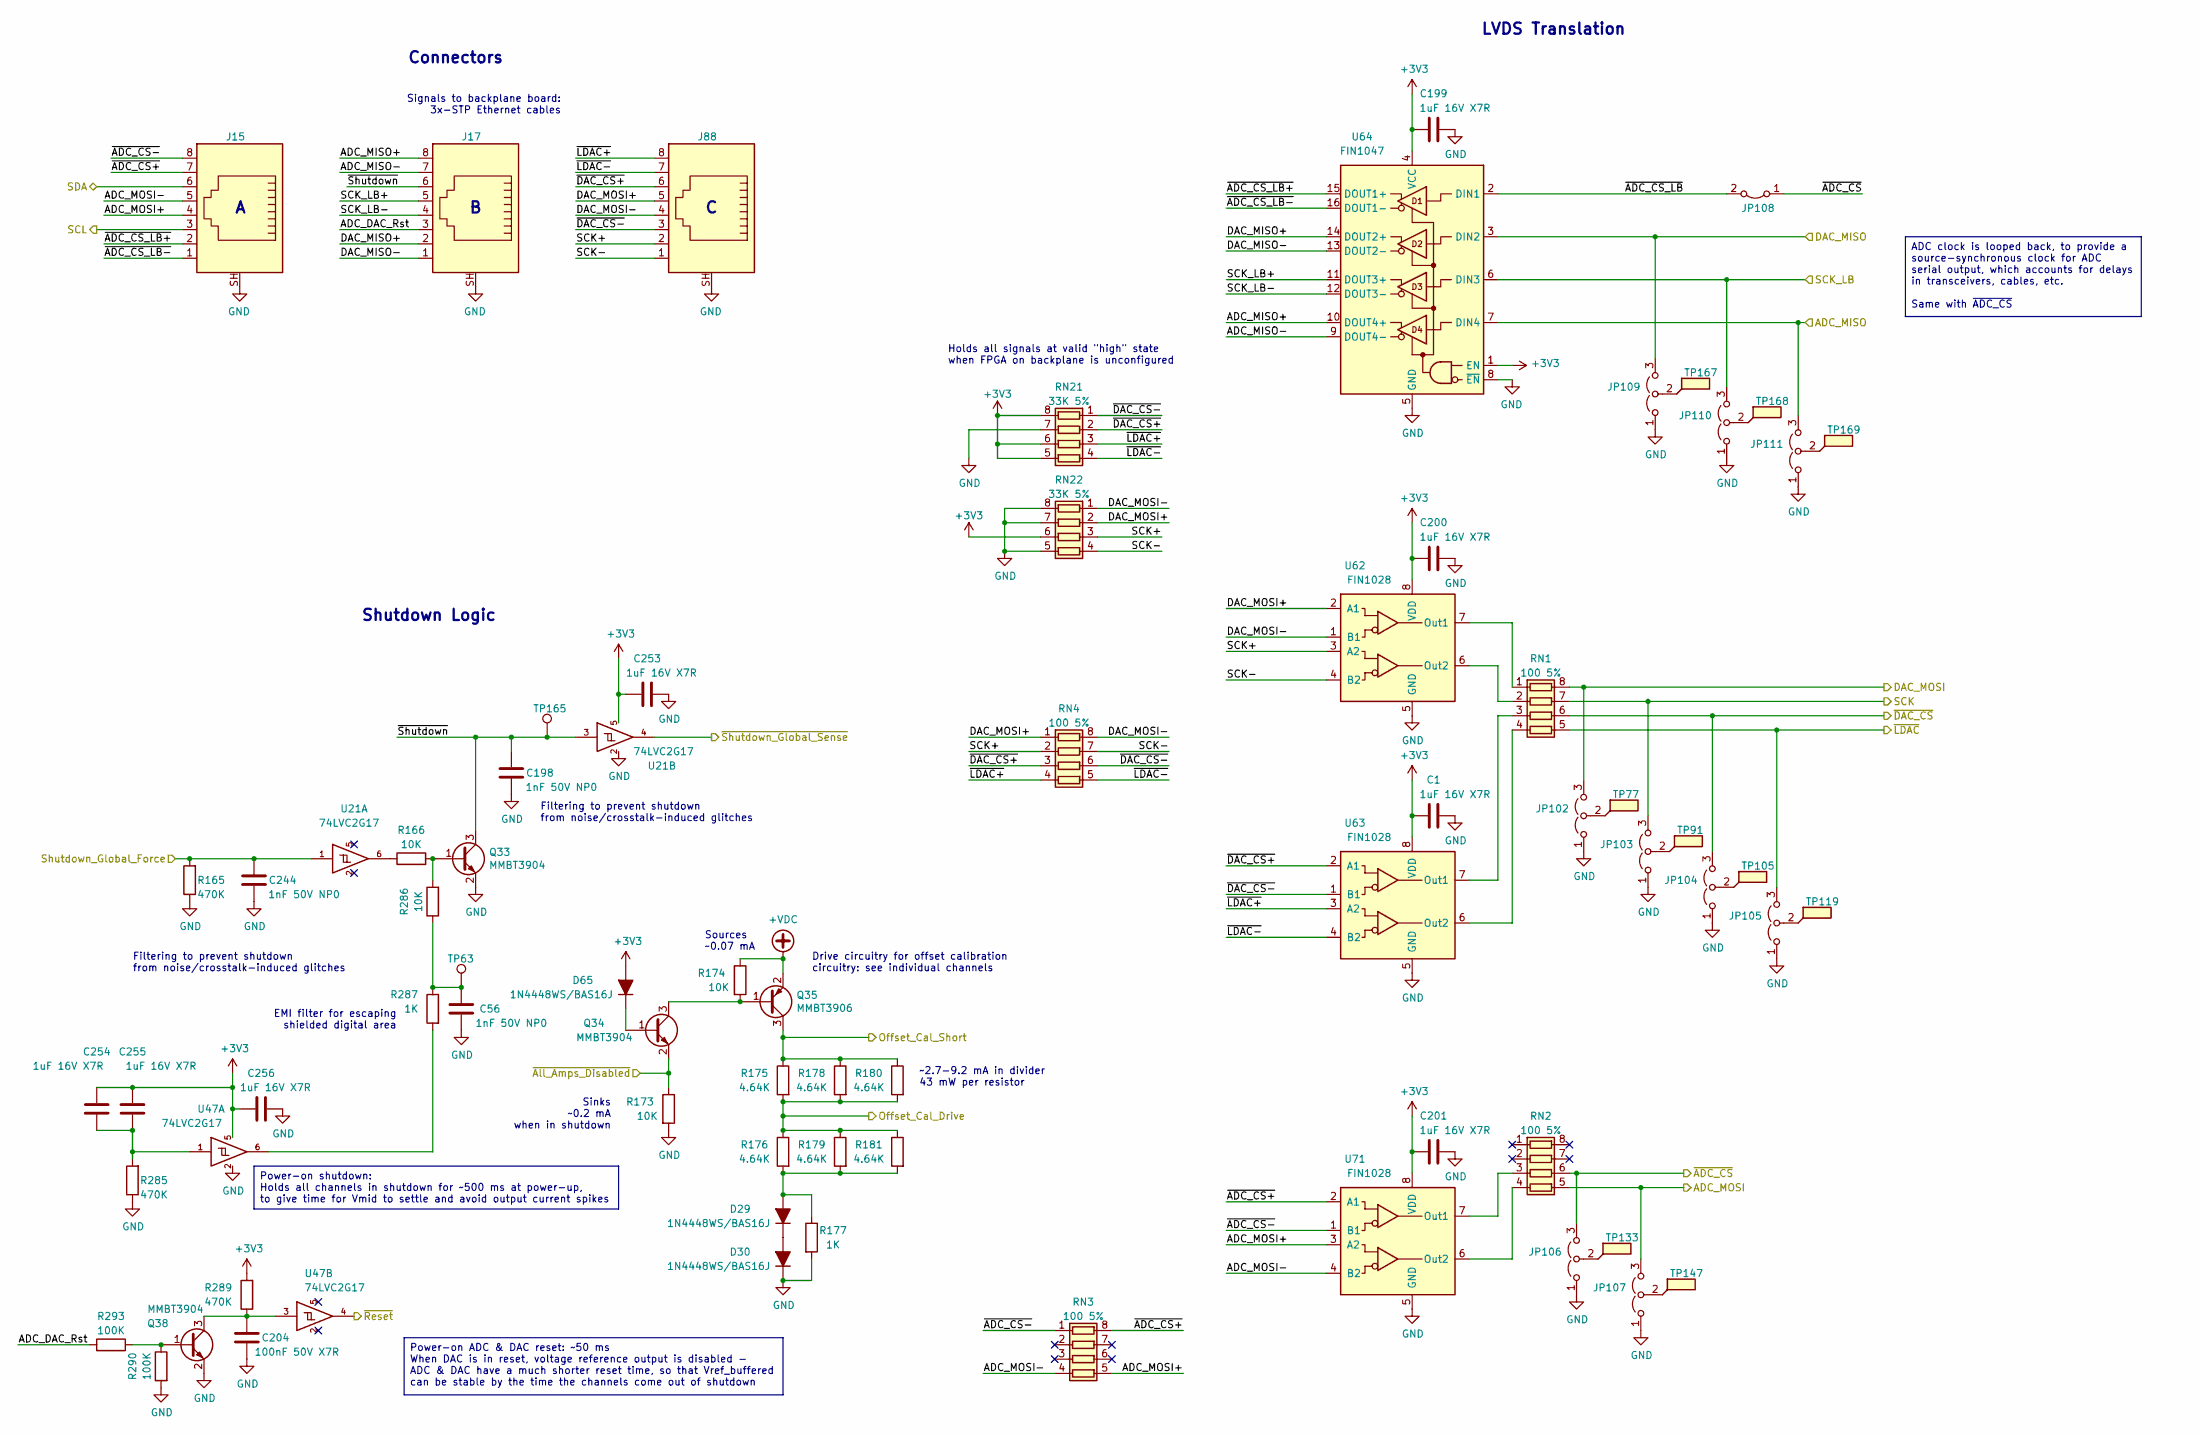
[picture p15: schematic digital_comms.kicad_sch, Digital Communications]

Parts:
C1, C199, C200, C201, C253, C254, C255, C256: 1uF 16V X7R; C_0603_1608Metric; MPN C0603C105K4RACTU
C56, C198, C244: 1nF 50V NP0; C_0603_1608Metric; MPN C0603C102J5GACTU
C204: 100nF 50V X7R; C_0603_1608Metric; MPN C0603C104K5RACTU
D29, D30, D65: 1N4448WS/BAS16J; D_SOD-323F; MPN BAS16J,115 / BAS16J,135
J15, J17, J88: RJ45_Shielded; RJ45_TE_x-406541-x_Horizontal; MPN 1-406541-8
JP102, JP103, JP104, JP105, JP106, JP107, JP109, JP110, JP111: Jumper_3_Open; SolderJumper-3_P2.0mm_Open_TrianglePad1.0x1.5mm
JP108: Jumper_2_Bridged; SolderJumper-2_P1.3mm_Bridged_RoundedPad1.0x1.5mm
Q33, Q34, Q38: MMBT3904; SOT-23; MPN MMBT3904-7-F
Q35: MMBT3906; SOT-23; MPN MMBT3906-7-F
R165, R285, R289: 470K; R_0805_2012Metric; MPN RK73H2ATTD4703F
R166, R173, R174, R286: 10K; R_0805_2012Metric; MPN RK73H2ATTD1002F
R175, R176, R178, R179, R180, R181: 4.64K; R_0805_2012Metric; MPN RK73H2ATTD4641F
R177, R287: 1K; R_0805_2012Metric; MPN RK73H2ATTD1001F
R290, R293: 100K; R_0805_2012Metric; MPN RK73H2ATTD1003F
RN1, RN2, RN3, RN4: 100 5%; R_Array_Concave_4x0603; MPN 742C083101JP
RN21, RN22: 33K 5%; R_Array_Concave_4x0603; MPN 742C083333JP
TP63, TP165: TestPoint; TestPoint_Pad_D2.0mm
TP77, TP91, TP105, TP119, TP133, TP147, TP167, TP168, TP169: TestPoint_Flag; TestPoint_Keystone_5019_Miniature; MPN 5019
U21, U47: 74LVC2G17; SOT-23-6; MPN 74LVC2G17GV,125
U62, U63, U71: FIN1028; SOIC-8_3.9x4.9mm_P1.27mm; MPN FIN1028MX
U64: FIN1047; TSSOP-16_4.4x5mm_P0.65mm; MPN FIN1047MTCX

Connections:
+3V3: C1.2, C199.2, C200.2, C201.2, C253.2, C254.2, C255.2, C256.2, D65.2 (A), R289.2, RN21.5 (R4.2), RN21.6 (R3.2), RN21.8 (R1.2), RN22.6 (R3.2), U21.5 (VCC), U47.5 (VCC), U62.8 (VDD), U63.8 (VDD), U64.1 (EN), U64.4 (VCC), U71.8 (VDD); also elsewhere on the board
+VDC: Q35.2 (E), R174.1; also elsewhere on the board
/Digital Communications/ADC_DAC_Rst: J17.3, R293.2
/Digital Communications/ADC_MISO: JP111.3 (B), U64.7 (DIN4); also elsewhere on the board
/Digital Communications/ADC_MISO+: J17.8, U64.10 (DOUT4+)
/Digital Communications/ADC_MISO-: J17.7, U64.9 (DOUT4-)
/Digital Communications/ADC_MOSI: JP107.3 (B), RN2.5 (R4.2); also elsewhere on the board
/Digital Communications/ADC_MOSI+: J15.4, RN3.5 (R4.2), U71.3 (A2)
/Digital Communications/ADC_MOSI-: J15.5, RN3.4 (R4.1), U71.4 (B2)
/Digital Communications/DAC_MISO: JP109.3 (B), U64.3 (DIN2); also elsewhere on the board
/Digital Communications/DAC_MISO+: J17.2, U64.14 (DOUT2+)
/Digital Communications/DAC_MISO-: J17.1, U64.13 (DOUT2-)
/Digital Communications/DAC_MOSI: JP102.3 (B), RN1.8 (R1.2); also elsewhere on the board
/Digital Communications/DAC_MOSI+: J88.5, RN4.1 (R1.1), RN22.2 (R2.1), U62.2 (A1)
/Digital Communications/DAC_MOSI-: J88.4, RN4.8 (R1.2), RN22.1 (R1.1), U62.1 (B1)
/Digital Communications/SCK: JP103.3 (B), RN1.7 (R2.2); also elsewhere on the board
/Digital Communications/SCK+: J88.2, RN4.2 (R2.1), RN22.3 (R3.1), U62.3 (A2)
/Digital Communications/SCK-: J88.1, RN4.7 (R2.2), RN22.4 (R4.1), U62.4 (B2)
/Digital Communications/SCK_LB: JP110.3 (B), U64.6 (DIN3); also elsewhere on the board
/Digital Communications/SCK_LB+: J17.5, U64.11 (DOUT3+)
/Digital Communications/SCK_LB-: J17.4, U64.12 (DOUT3-)
/Digital Communications/SCL: J15.3; also elsewhere on the board
/Digital Communications/SDA: J15.6; also elsewhere on the board
/Digital Communications/~ADC_CS+: J15.7, RN3.8 (R1.2), U71.2 (A1)
/Digital Communications/~ADC_CS-: J15.8, RN3.1 (R1.1), U71.1 (B1)
/Digital Communications/~ADC_CS_LB+: J15.2, U64.15 (DOUT1+)
/Digital Communications/~ADC_CS_LB-: J15.1, U64.16 (DOUT1-)
/Digital Communications/~ADC_CS_LB: JP108.2 (B), U64.2 (DIN1)
/Digital Communications/~ADC_CS: JP106.3 (B), JP108.1 (A), RN2.6 (R3.2); also elsewhere on the board
/Digital Communications/~DAC_CS+: J88.6, RN4.3 (R3.1), RN21.2 (R2.1), U63.2 (A1)
/Digital Communications/~DAC_CS-: J88.3, RN4.6 (R3.2), RN21.1 (R1.1), U63.1 (B1)
/Digital Communications/~DAC_CS: JP104.3 (B), RN1.6 (R3.2); also elsewhere on the board
/Digital Communications/~LDAC+: J88.8, RN4.4 (R4.1), RN21.3 (R3.1), U63.3 (A2)
/Digital Communications/~LDAC-: J88.7, RN4.5 (R4.2), RN21.4 (R4.1), U63.4 (B2)
/Digital Communications/~LDAC: JP105.3 (B), RN1.5 (R4.2); also elsewhere on the board
/Digital Communications/~Shutdown: C198.2, J17.6, Q33.3 (C), TP165.1 (1_1), U21.3
/Digital Controls/~Reset: U47.4; also elsewhere on the board
/Offset_Cal_Drive: R175.2, R176.1, R178.2, R179.1, R180.2, R181.1; also elsewhere on the board
/Offset_Cal_Short: Q35.3 (C), R175.1, R178.1, R180.1; also elsewhere on the board
/Shutdown_Global_Force: C244.2, R165.2, U21.1; also elsewhere on the board
/~All_Amps_Disabled: Q34.2 (E), R173.1; also elsewhere on the board
/~Shutdown_Global_Sense: U21.4; also elsewhere on the board
GND: C1.1, C56.1, C198.1, C199.1, C200.1, C201.1, C204.1, C244.1, C253.1, C256.1, D30.1 (K), J15.SH, J17.SH, J88.SH, JP102.1 (A), JP103.1 (A), JP104.1 (A), JP105.1 (A), JP106.1 (A), JP107.1 (A), JP109.1 (A), JP110.1 (A), JP111.1 (A), Q33.2 (E), Q38.2 (E), R165.1, R173.2, R177.2, R285.1, R290.2, RN21.7 (R2.2), RN22.5 (R4.2), RN22.7 (R2.2), RN22.8 (R1.2), U21.2 (GND), U47.2 (GND), U62.5 (GND), U63.5 (GND), U64.5 (GND), U64.8 (~EN), U71.5 (GND); also elsewhere on the board
unnamed: C56.2, R286.1, R287.1, TP63.1 (1_1)
unnamed: C254.1, C255.1, R285.2, U47.1
unnamed: D29.2 (A), R176.2, R177.1, R179.2, R181.2
unnamed: D29.1 (K), D30.2 (A)
unnamed: D65.1 (K), Q34.1 (B)
unnamed: JP102.2 (C), TP77.1 (1_1)
unnamed: JP103.2 (C), TP91.1 (1_1)
unnamed: JP104.2 (C), TP105.1 (1_1)
unnamed: JP105.2 (C), TP119.1 (1_1)
unnamed: JP106.2 (C), TP133.1 (1_1)
unnamed: JP107.2 (C), TP147.1 (1_1)
unnamed: JP109.2 (C), TP167.1 (1_1)
unnamed: JP110.2 (C), TP168.1 (1_1)
unnamed: JP111.2 (C), TP169.1 (1_1)
unnamed: Q33.1 (B), R166.2, R286.2
unnamed: Q34.3 (C), Q35.1 (B), R174.2
unnamed: Q38.1 (B), R290.1, R293.1
unnamed: C204.2, Q38.3 (C), R289.1, U47.3
unnamed: R166.1, U21.6
unnamed: R287.2, U47.6
unnamed: RN1.1 (R1.1), U62.7 (Out1)
unnamed: RN1.2 (R2.1), U62.6 (Out2)
unnamed: RN1.3 (R3.1), U63.7 (Out1)
unnamed: RN1.4 (R4.1), U63.6 (Out2)
unnamed: RN2.3 (R3.1), U71.7 (Out1)
unnamed: RN2.4 (R4.1), U71.6 (Out2)

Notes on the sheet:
Filtering to prevent shutdown from noise/crosstalk-induced glitches
Sources ~0.07 mA
Drive circuitry for offset calibration circuitry: see individual channels
Signals to backplane board: 3x-STP Ethernet cables
Holds all signals at valid "high" state when FPGA on backplane is unconfigured
EMI filter for escaping shielded digital area
Shutdown Logic
~2.7-9.2 mA in divider 43 mW per resistor
Sinks ~0.2 mA when in shutdown
LVDS Translation
Connectors
Power-on shutdown: Holds all channels in shutdown for ~500 ms at power-up, to give time for Vmid to settle and avoid output current spikes
Power-on ADC & DAC reset: ~50 ms When DAC is in reset, voltage reference output is disabled - ADC & DAC have a much shorter reset time, so that Vref_buffered can be stable by the time the channels come out of shutdown
ADC clock is looped back, to provide a source-synchronous clock for ADC serial output, which accounts for delays in transceivers, cables, etc. Same with ~{ADC_CS}

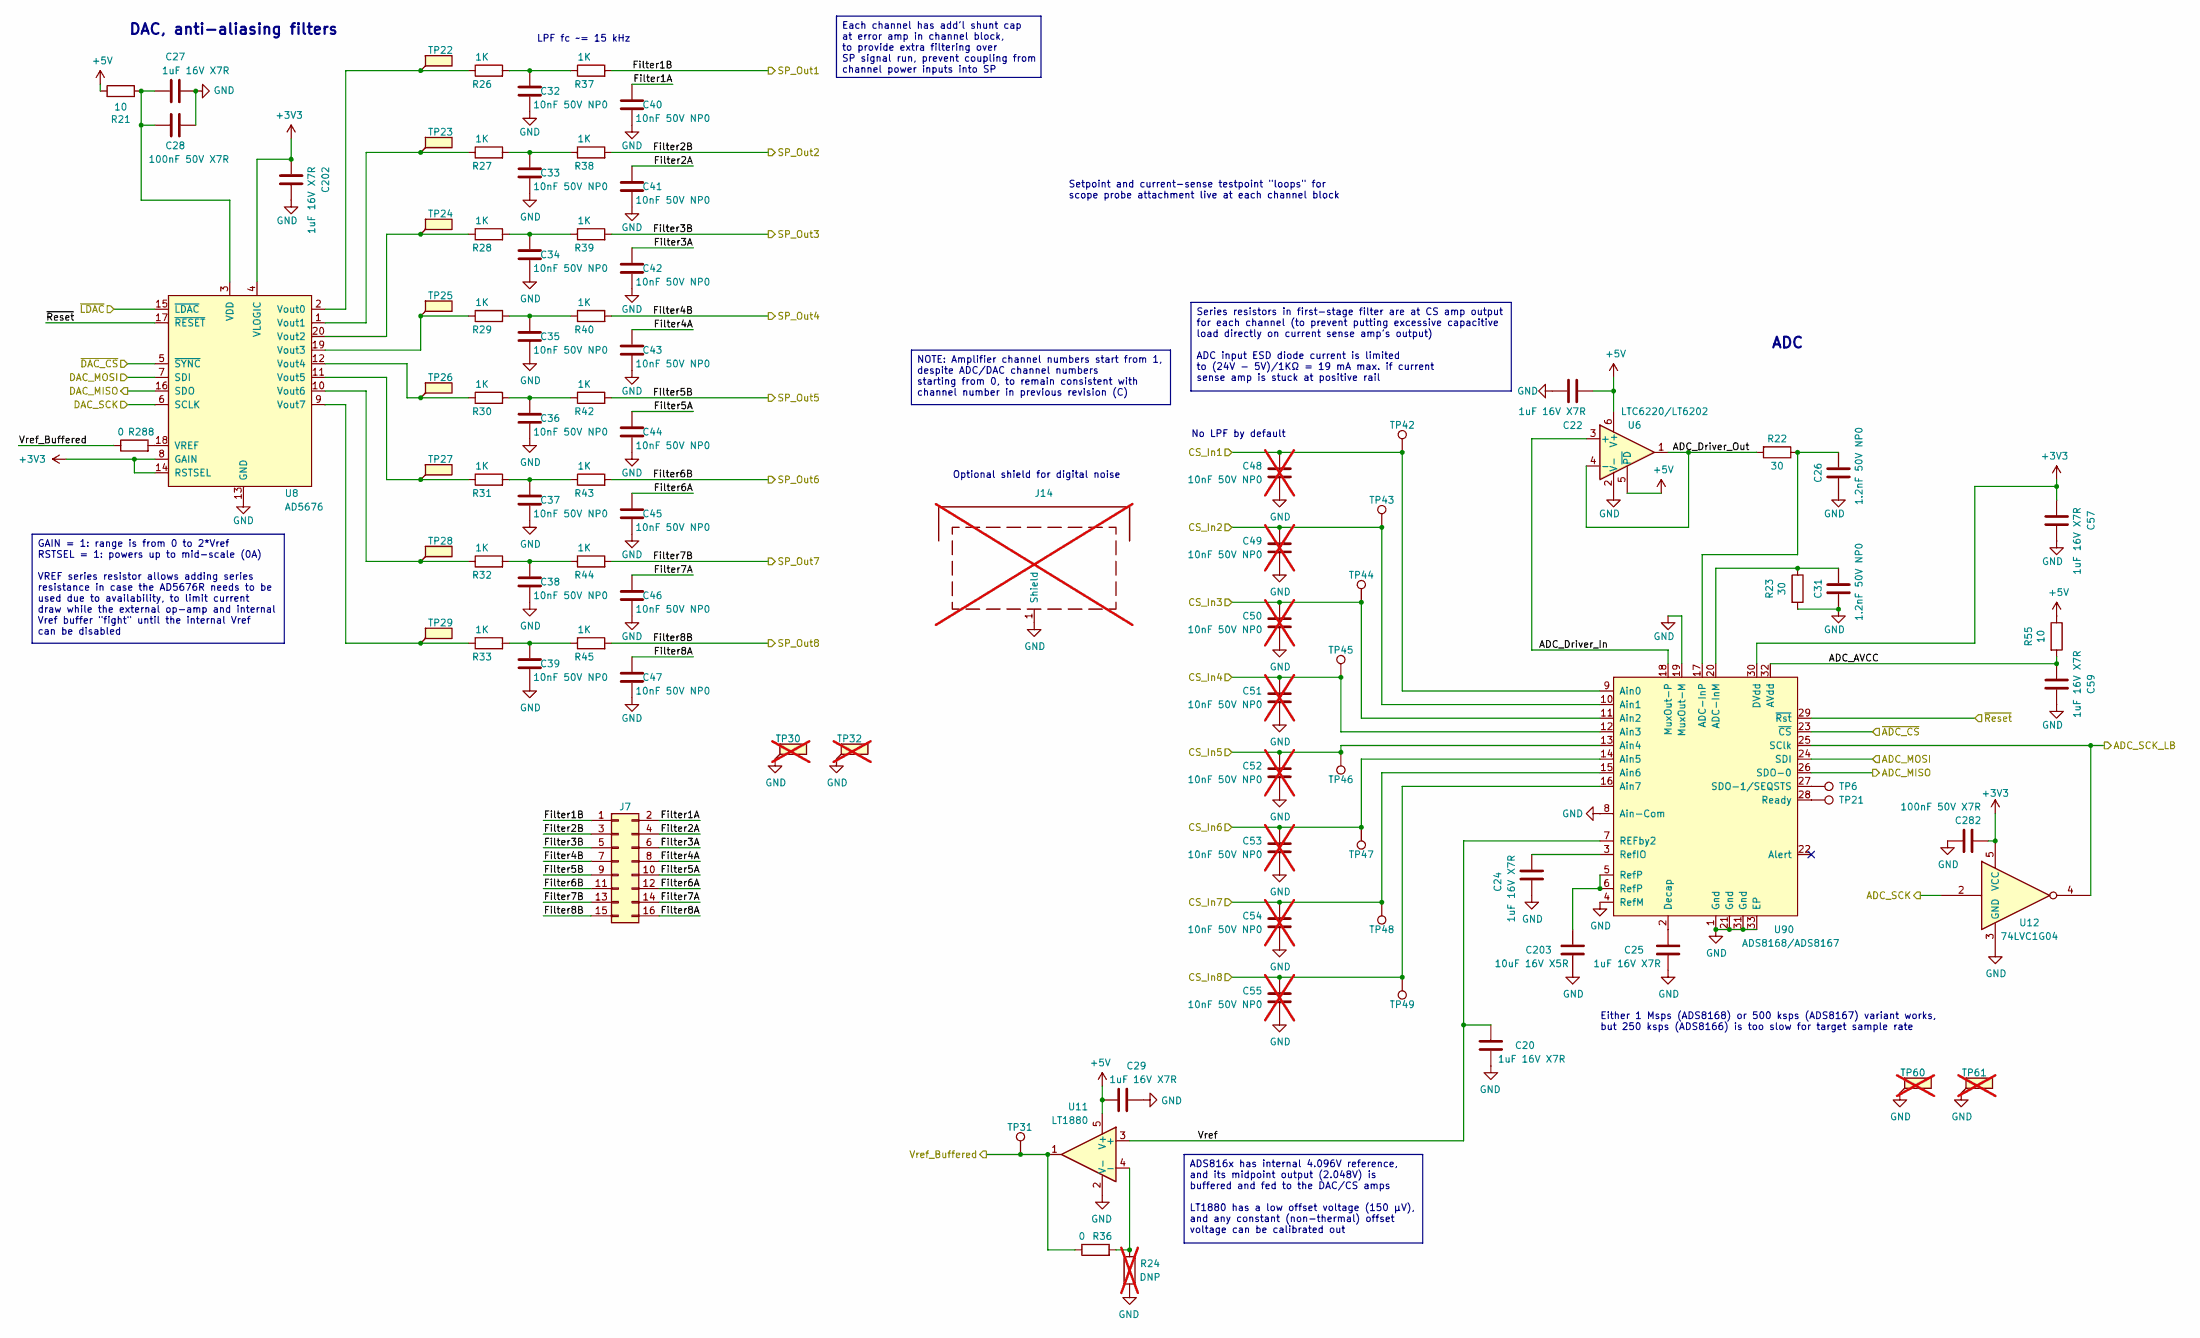
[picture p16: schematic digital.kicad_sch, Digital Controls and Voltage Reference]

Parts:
C20, C22, C24, C25, C27, C29, C57, C59, C202: 1uF 16V X7R; C_0603_1608Metric; MPN C0603C105K4RACTU
C26, C31: 1.2nF 50V NP0; C_0603_1608Metric; MPN GRM1885C1H122JA01J
C28, C282: 100nF 50V X7R; C_0603_1608Metric; MPN C0603C104K5RACTU
C32, C33, C34, C35, C36, C37, C38, C39, C40, C41, C42, C43, C44, C45, C46, C47: 10nF 50V NP0; C_0603_1608Metric; MPN GRM1885C1H103JA01D
C48, C49, C50, C51, C52, C53, C54, C55: 10nF 50V NP0; C_0603_1608Metric; MPN GRM1885C1H103JA01D; not fitted
C203: 10uF 16V X5R; C_0805_2012Metric; MPN C0805C106M4PACTU
J7: Conn_02x08_Odd_Even; PinHeader_2x08_P2.54mm_Vertical
J14: RF_Shield_Two_Pieces; Shield_44x47mm; not fitted
R21, R55: 10; R_0805_2012Metric; MPN RK73H2ATTD10R0F
R22, R23: 30; R_0805_2012Metric; MPN RK73H2ATTD30R0F
R24: DNP; R_0805_2012Metric; not fitted
R26, R27, R28, R29, R30, R31, R32, R33, R37, R38, R39, R40, R42, R43, R44, R45: 1K; R_0805_2012Metric; MPN RK73H2ATTD1001F
R36, R288: 0; R_0805_2012Metric; MPN 5106
TP6, TP21: TestPoint_Flag; TestPoint_Pad_1.0x1.0mm
TP22, TP23, TP24, TP25, TP26, TP27, TP28, TP29: TestPoint_Flag; TestPoint_Keystone_5019_Miniature; MPN 5019
TP30, TP32, TP60, TP61: TestPoint_Flag; TestPoint_Keystone_5019_Miniature; MPN 5019; not fitted
TP31: TestPoint; TestPoint_Pad_D2.0mm
TP42, TP43, TP44, TP45, TP46, TP47, TP48, TP49: TestPoint; TestPoint_Pad_1.0x1.0mm
U6: LTC6220/LT6202; SOT-23-6; MPN LT6220CS5#TRMPBF
U8: AD5676; TSSOP-20_4.4x6.5mm_P0.65mm; MPN AD5676ARUZ-REEL7
U11: LT1880; SOT-23-5; MPN LT1880IS5#TRMPBF
U12: 74LVC1G04; SOT-23-5; MPN SN74LVC1G04DBVR
U90: ADS8168/ADS8167; VQFN-32-1EP_5x5mm_P0.5mm_EP3.45x3.45mm; MPN ADS8168IRHBT

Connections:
+3V3: C57.2, C202.2, C282.1, U8.4 (VLOGIC), U8.8 (GAIN), U8.14 (RSTSEL), U12.5 (VCC), U90.30 (DVdd); also elsewhere on the board
+5V: C22.2, C29.1, R21.1, R55.1, U6.5 (~PD), U6.6 (V+), U11.5 (V+); also elsewhere on the board
/Channel 1/CS: C48.2, TP42.1 (1_1), U90.9 (Ain0); also elsewhere on the board
/Channel 2/CS: C49.2, TP43.1 (1_1), U90.10 (Ain1); also elsewhere on the board
/Channel 3/CS: C50.2, TP44.1 (1_1), U90.11 (Ain2); also elsewhere on the board
/Channel 4/CS: C51.2, TP45.1 (1_1), U90.12 (Ain3); also elsewhere on the board
/Channel 5/CS: C52.2, TP46.1 (1_1), U90.13 (Ain4); also elsewhere on the board
/Channel 6/CS: C53.2, TP47.1 (1_1), U90.14 (Ain5); also elsewhere on the board
/Channel 7/CS: C54.2, TP48.1 (1_1), U90.15 (Ain6); also elsewhere on the board
/Channel 8/CS: C55.2, TP49.1 (1_1), U90.16 (Ain7); also elsewhere on the board
/Digital Communications/ADC_MISO: U90.26 (SDO-0); also elsewhere on the board
/Digital Communications/ADC_MOSI: U90.24 (SDI); also elsewhere on the board
/Digital Communications/DAC_MISO: U8.16 (SDO); also elsewhere on the board
/Digital Communications/DAC_MOSI: U8.7 (SDI); also elsewhere on the board
/Digital Communications/SCK: U8.6 (SCLK), U12.2; also elsewhere on the board
/Digital Communications/SCK_LB: U12.4, U90.25 (SClk); also elsewhere on the board
/Digital Communications/~ADC_CS: U90.23 (~CS); also elsewhere on the board
/Digital Communications/~DAC_CS: U8.5 (~SYNC); also elsewhere on the board
/Digital Communications/~LDAC: U8.15 (~LDAC); also elsewhere on the board
/Digital Controls/ADC_AVCC: C59.2, R55.2, U90.32 (AVdd)
/Digital Controls/ADC_Driver_In: U6.3 (+), U90.18 (MuxOut-P)
/Digital Controls/ADC_Driver_Out: R22.2, U6.1, U6.4 (-)
/Digital Controls/Filter1A: C40.2, J7.2
/Digital Controls/Filter1B: J7.1, R37.2; also elsewhere on the board
/Digital Controls/Filter2A: C41.2, J7.4
/Digital Controls/Filter2B: J7.3, R38.2; also elsewhere on the board
/Digital Controls/Filter3A: C42.2, J7.6
/Digital Controls/Filter3B: J7.5, R39.2; also elsewhere on the board
/Digital Controls/Filter4A: C43.2, J7.8
/Digital Controls/Filter4B: J7.7, R40.2; also elsewhere on the board
/Digital Controls/Filter5A: C44.2, J7.10
/Digital Controls/Filter5B: J7.9, R42.2; also elsewhere on the board
/Digital Controls/Filter6A: C45.2, J7.12
/Digital Controls/Filter6B: J7.11, R43.2; also elsewhere on the board
/Digital Controls/Filter7A: C46.2, J7.14
/Digital Controls/Filter7B: J7.13, R44.2; also elsewhere on the board
/Digital Controls/Filter8A: C47.2, J7.16
/Digital Controls/Filter8B: J7.15, R45.2; also elsewhere on the board
/Digital Controls/Vref: C20.1, U11.3 (+), U90.7 (REFby2)
/Digital Controls/~Reset: U8.17 (~RESET), U90.29 (~Rst); also elsewhere on the board
/Vref_Buffered: R36.1, R288.1, TP31.1 (1_1), U11.1; also elsewhere on the board
GND: C20.2, C22.1, C24.2, C25.2, C26.2, C27.1, C28.1, C29.2, C31.2, C32.1, C33.1, C34.1, C35.1, C36.1, C37.1, C38.1, C39.1, C40.1, C41.1, C42.1, C43.1, C44.1, C45.1, C46.1, C47.1, C48.1, C49.1, C50.1, C51.1, C52.1, C53.1, C54.1, C55.1, C57.1, C59.1, C202.1, C203.2, C282.2, J14.1 (Shield_1), R23.2, R24.2, TP30.1 (1_1), TP32.1 (1_1), TP60.1 (1_1), TP61.1 (1_1), U6.2 (V-), U8.13 (GND), U11.2 (V-), U12.3 (GND), U90.1 (Gnd), U90.4 (RefM), U90.8 (Ain-Com), U90.19 (MuxOut-M), U90.21 (Gnd), U90.31 (Gnd), U90.33 (EP); also elsewhere on the board
unnamed: C32.2, R26.2, R37.1
unnamed: C33.2, R27.2, R38.1
unnamed: C34.2, R28.2, R39.1
unnamed: C35.2, R29.2, R40.1
unnamed: C36.2, R30.2, R42.1
unnamed: C37.2, R31.2, R43.1
unnamed: C38.2, R32.2, R44.1
unnamed: C39.2, R33.2, R45.1
unnamed: C203.1, U90.5 (RefP), U90.6 (RefP)
unnamed: C27.2, C28.2, R21.2, U8.3 (VDD)
unnamed: R288.2, U8.18 (VREF)
unnamed: R26.1, TP22.1 (1_1), U8.2 (Vout0)
unnamed: R27.1, TP23.1 (1_1), U8.1 (Vout1)
unnamed: R28.1, TP24.1 (1_1), U8.20 (Vout2)
unnamed: R29.1, TP25.1 (1_1), U8.19 (Vout3)
unnamed: R30.1, TP26.1 (1_1), U8.12 (Vout4)
unnamed: R31.1, TP27.1 (1_1), U8.11 (Vout5)
unnamed: R32.1, TP28.1 (1_1), U8.10 (Vout6)
unnamed: R33.1, TP29.1 (1_1), U8.9 (Vout7)
unnamed: R24.1, R36.2, U11.4 (-)
unnamed: C31.1, R23.1, U90.20 (ADC-InM)
unnamed: C26.1, R22.1, U90.17 (ADC-InP)
unnamed: C25.1, U90.2 (Decap)
unnamed: TP21.1 (1_1), U90.28 (Ready)
unnamed: C24.1, U90.3 (RefIO)
unnamed: TP6.1 (1_1), U90.27 (SDO-1/SEQSTS)

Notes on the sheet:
No LPF by default
ADC
Either 1 Msps (ADS8168) or 500 ksps (ADS8167) variant works, but 250 ksps (ADS8166) is too slow for target sample rate
Setpoint and current-sense testpoint "loops" for scope probe attachment live at each channel block
DAC, anti-aliasing filters
Optional shield for digital noise
LPF fc ~= 15 kHz
NOTE: Amplifier channel numbers start from 1, despite ADC/DAC channel numbers starting from 0, to remain consistent with channel number in previous revision (C)
GAIN = 1: range is from 0 to 2*Vref RSTSEL = 1: powers up to mid-scale (0A) VREF series resistor allows adding series resistance in case the AD5676R needs to be used due to availability, to limit current draw while the external op-amp and internal Vref buffer "fight" until the internal Vref can be 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
Each channel has add'l shunt cap at error amp in channel block, to provide extra filtering over SP signal run, prevent coupling from channel power inputs into SP
Series resistors in first-stage filter are at CS amp output for each channel (to prevent putting excessive capacitive load directly on current sense amp's output) ADC input ESD diode current is limited to (24V - 5V)/1KΩ = 19 mA max. if current sense amp is stuck at positive rail
ADS816x has internal 4.096V reference, and its midpoint output (2.048V) is buffered and fed to the DAC/CS amps LT1880 has a low offset voltage (150 µV), and any constant (non-thermal) offset voltage can be calibrated out

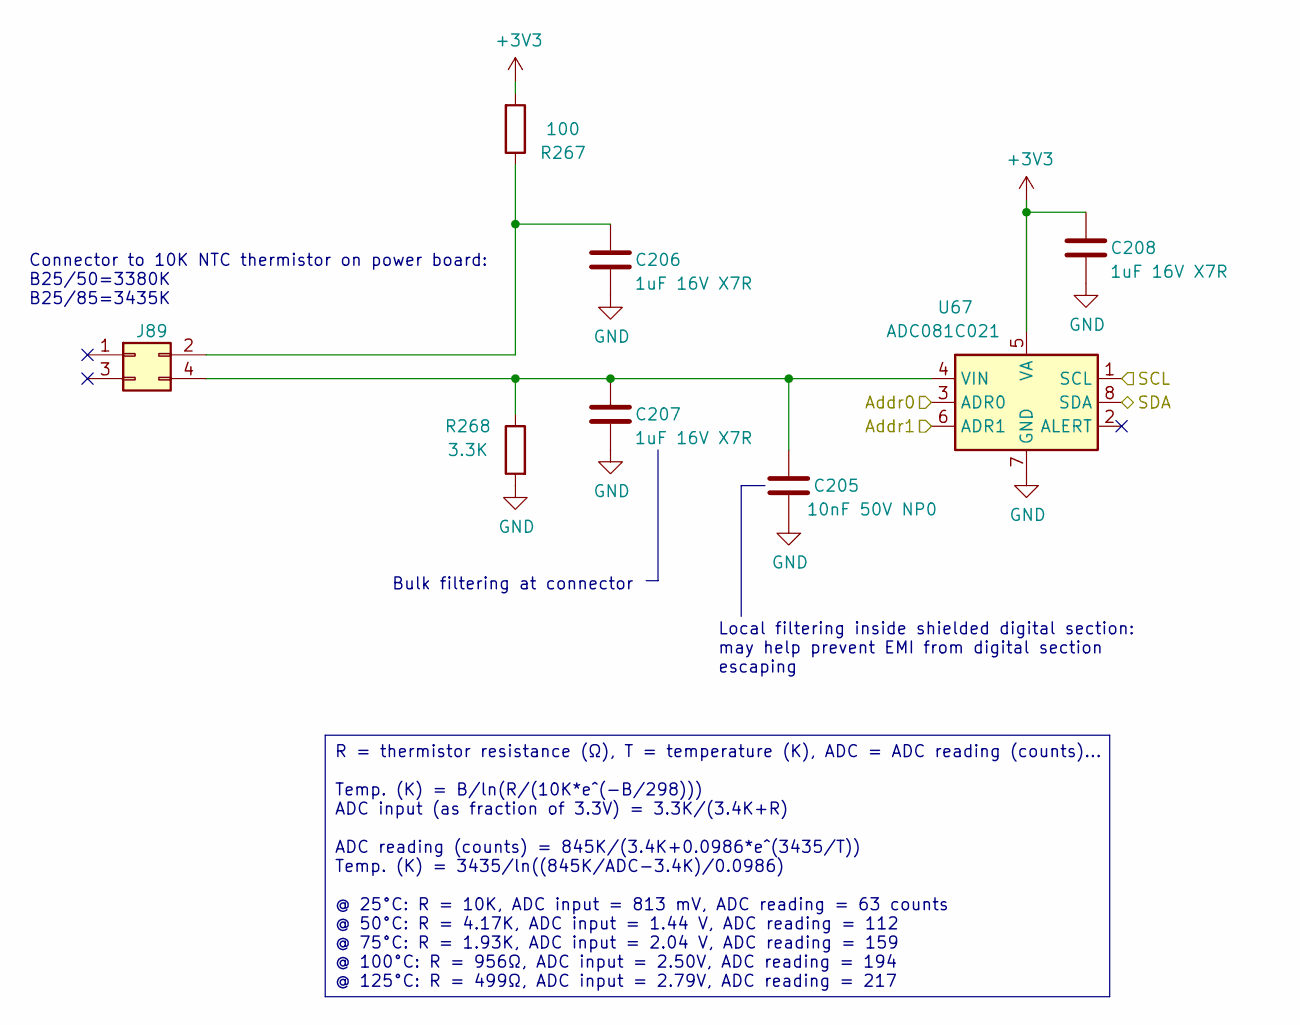
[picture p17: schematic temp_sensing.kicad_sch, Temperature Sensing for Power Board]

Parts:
C205: 10nF 50V NP0; C_0603_1608Metric; MPN GRM1885C1H103JA01D
C206, C207, C208: 1uF 16V X7R; C_0603_1608Metric; MPN C0603C105K4RACTU
J89: Conn_02x02; PinSocket_2x02_P2.54mm_Vertical_SMD_BotEntry_Pin; MPN M20-7810245 / M20-7810245R
R267: 100; R_0805_2012Metric; MPN RK73H2ATTD1000F
R268: 3.3K; R_0805_2012Metric; MPN RK73H2ATTD3301F
U67: ADC081C021; MSOP-8_3x3mm_P0.65mm; MPN ADC081C021CIMM/NOPB

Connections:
+3V3: C208.2, R267.2, U67.5 (VA); also elsewhere on the board
/Digital Communications/SCL: U67.1 (SCL); also elsewhere on the board
/Digital Communications/SDA: U67.8 (SDA); also elsewhere on the board
/Left Temp. Sensor/Addr0: U67.3 (ADR0); also elsewhere on the board
/Left Temp. Sensor/Addr1: U67.6 (ADR1); also elsewhere on the board
GND: C205.1, C206.1, C207.1, C208.1, R268.2, U67.7 (GND); also elsewhere on the board
unnamed: C206.2, J89.2, R267.1
unnamed: C205.2, C207.2, J89.4, R268.1, U67.4 (VIN)

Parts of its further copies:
C209, C210, C211, C212, C213, C214: 1uF 16V X7R; C_0603_1608Metric; MPN C0603C105K4RACTU
C233, C234: 10nF 50V NP0; C_0603_1608Metric; MPN GRM1885C1H103JA01D
J90, J91: Conn_02x02; PinSocket_2x02_P2.54mm_Vertical_SMD_BotEntry_Pin; MPN M20-7810245 / M20-7810245R
R269, R271: 100; R_0805_2012Metric; MPN RK73H2ATTD1000F
R270, R272: 3.3K; R_0805_2012Metric; MPN RK73H2ATTD3301F
U68, U69: ADC081C021; MSOP-8_3x3mm_P0.65mm; MPN ADC081C021CIMM/NOPB

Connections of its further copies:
+3V3: C211.2, C214.2, R269.2, R271.2, U68.5 (VA), U69.5 (VA); also elsewhere on the board
/Digital Communications/SCL: U68.1 (SCL), U69.1 (SCL); also elsewhere on the board
/Digital Communications/SDA: U68.8 (SDA), U69.8 (SDA); also elsewhere on the board
/Mid. Temp. Sensor/Addr0: U68.3 (ADR0); also elsewhere on the board
/Mid. Temp. Sensor/Addr1: U68.6 (ADR1); also elsewhere on the board
/Right Temp. Sensor/Addr0: U69.3 (ADR0); also elsewhere on the board
/Right Temp. Sensor/Addr1: U69.6 (ADR1); also elsewhere on the board
GND: C209.1, C210.1, C211.1, C212.1, C213.1, C214.1, C233.1, C234.1, R270.2, R272.2, U68.7 (GND), U69.7 (GND); also elsewhere on the board
unnamed: C209.2, J90.2, R269.1
unnamed: C210.2, C233.2, J90.4, R270.1, U68.4 (VIN)
unnamed: C212.2, J91.2, R271.1
unnamed: C213.2, C234.2, J91.4, R272.1, U69.4 (VIN)

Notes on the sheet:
Connector to 10K NTC thermistor on power board: B25/50=3380K B25/85=3435K
Bulk filtering at connector
Local filtering inside shielded digital section: may help prevent EMI from digital section escaping
R = thermistor resistance (Ω), T = temperature (K), ADC = ADC reading (counts)... Temp. (K) = B/ln(R/(10K*e^(-B/298))) ADC input (as fraction of 3.3V) = 3.3K/(3.4K+R) ADC reading (counts) = 845K/(3.4K+0.0986*e^(3435/T)) Temp. (K) = 3435/ln((845K/ADC-3.4K)/0.0986) @ 25°C: R = 10K, ADC input = 813 mV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

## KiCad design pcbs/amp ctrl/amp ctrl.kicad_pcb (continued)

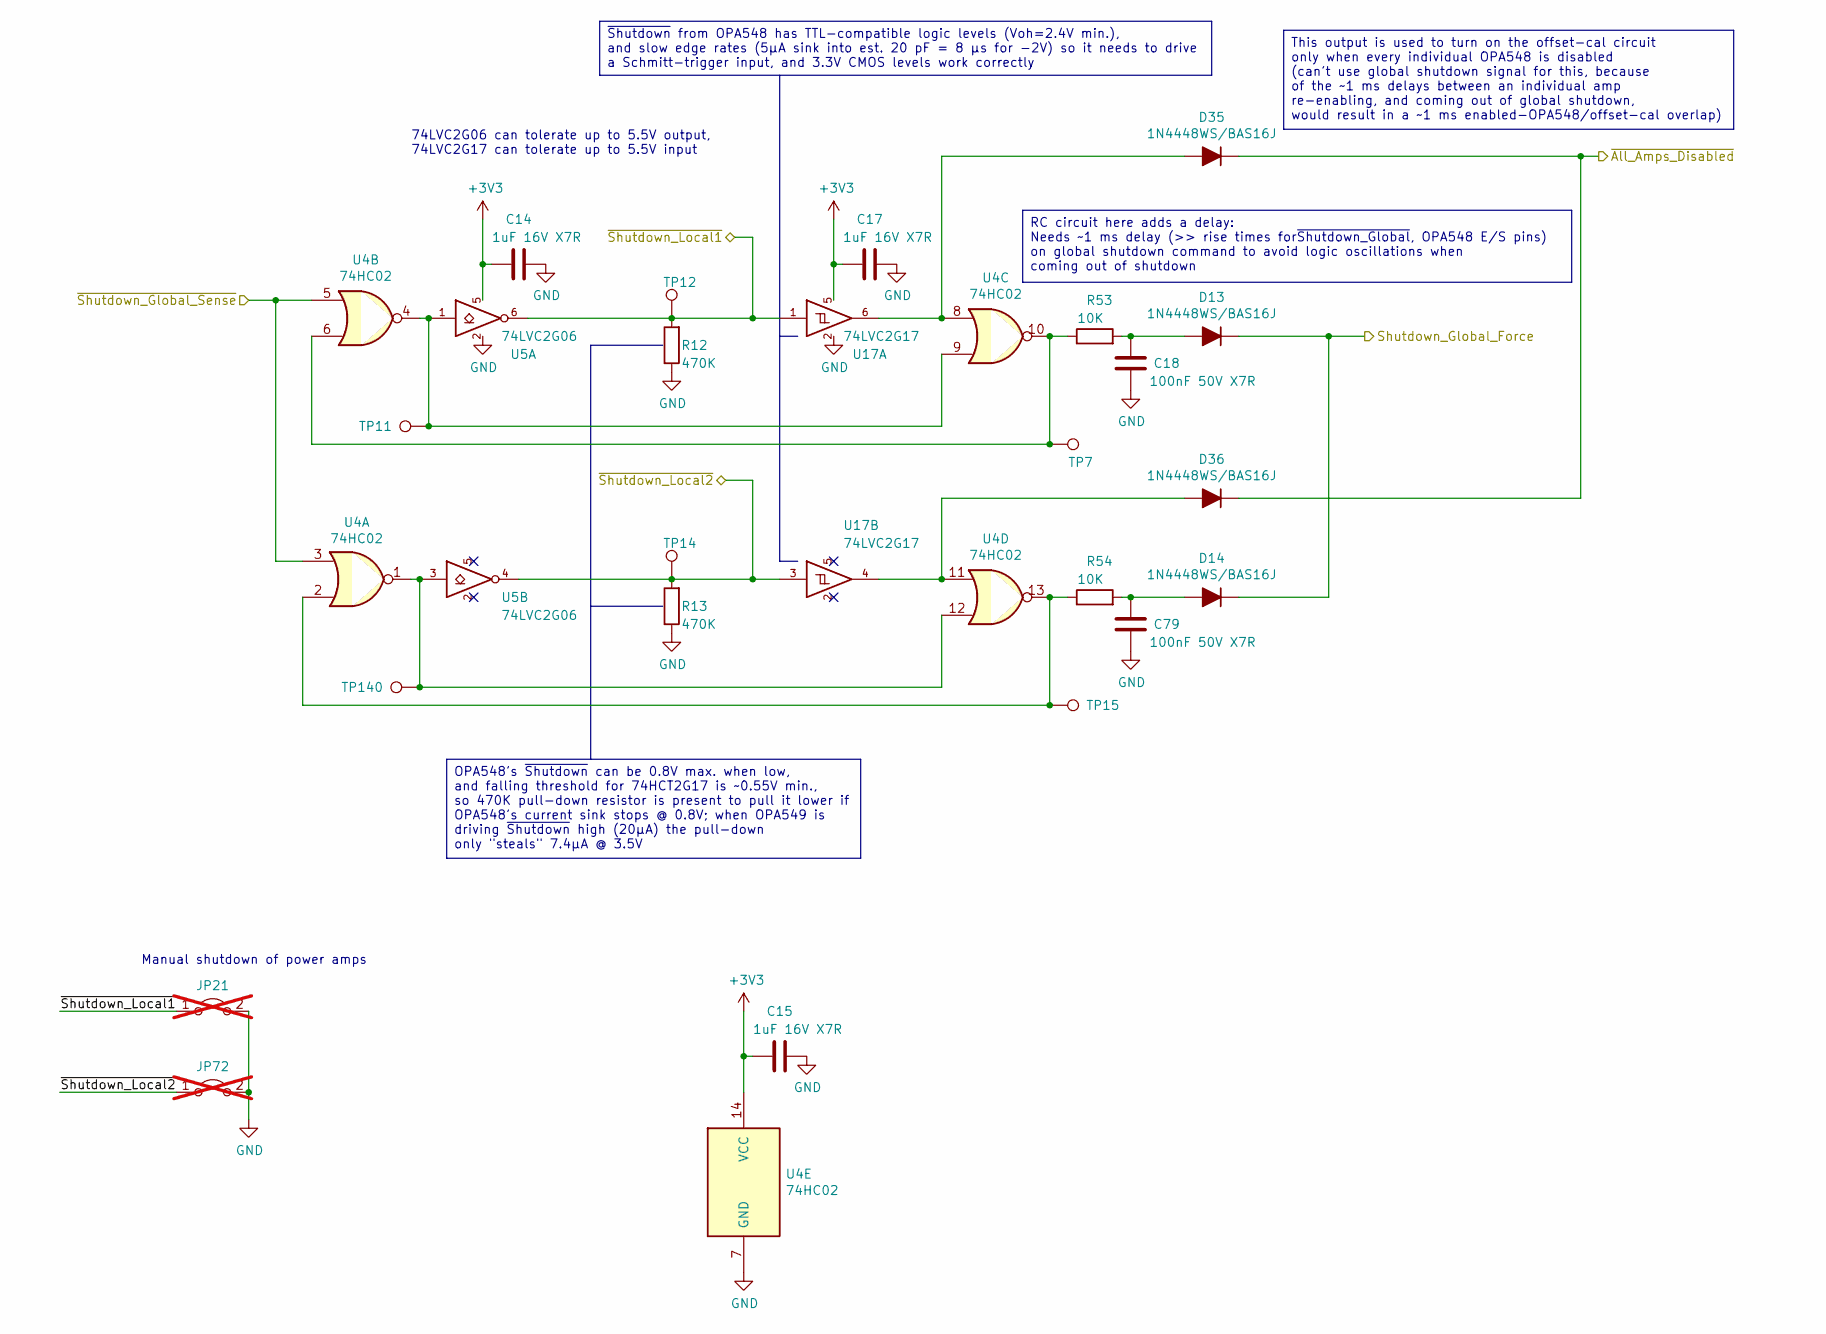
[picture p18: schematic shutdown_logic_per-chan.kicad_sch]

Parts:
C14, C15, C17: 1uF 16V X7R; C_0603_1608Metric; MPN C0603C105K4RACTU
C18, C79: 100nF 50V X7R; C_0603_1608Metric; MPN C0603C104K5RACTU
D13, D14, D35, D36: 1N4448WS/BAS16J; D_SOD-323F; MPN BAS16J,115 / BAS16J,135
JP21, JP72: PinHeader_1x02_P2.54mm_Vertical; not fitted
R12, R13: 470K; R_0805_2012Metric; MPN RK73H2ATTD4703F
R53, R54: 10K; R_0805_2012Metric; MPN RK73H2ATTD1002F
TP7, TP11, TP12, TP14, TP15, TP140: TestPoint; TestPoint_Pad_D1.5mm
U4: 74HC02; TSSOP-14_4.4x5mm_P0.65mm; MPN 74VHC02FT
U5: 74LVC2G06; SOT-23-6; MPN 74LVC2G06GV,125
U17: 74LVC2G17; SOT-23-6; MPN 74LVC2G17GV,125

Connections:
+3V3: C14.2, C15.2, C17.2, U4.14 (VCC), U5.5 (VCC), U17.5 (VCC); also elsewhere on the board
/Channel 1/~Shutdown1: JP21.1 (A), R12.2, TP12.1 (1_1), U5.6, U17.1; also elsewhere on the board
/Channel 1/~Shutdown2: JP72.1 (A), R13.2, TP14.1 (1_1), U5.4, U17.3; also elsewhere on the board
/Shutdown_Global_Force: D13.1 (K), D14.1 (K); also elsewhere on the board
/~All_Amps_Disabled: D35.1 (K), D36.1 (K); also elsewhere on the board
/~Shutdown_Global_Sense: U4.3, U4.5; also elsewhere on the board
GND: C14.1, C15.1, C17.1, C18.2, C79.2, JP21.2 (B), JP72.2 (B), R12.1, R13.1, U4.7 (GND), U5.2 (GND), U17.2 (GND); also elsewhere on the board
unnamed: C18.1, D13.2 (A), R53.2
unnamed: C79.1, D14.2 (A), R54.2
unnamed: D35.2 (A), U4.8, U17.6
unnamed: D36.2 (A), U4.11, U17.4
unnamed: R53.1, TP7.1 (1_1), U4.6, U4.10
unnamed: R54.1, TP15.1 (1_1), U4.2, U4.13
unnamed: TP11.1 (1_1), U4.4, U4.9, U5.1
unnamed: TP140.1 (1_1), U4.1, U4.12, U5.3

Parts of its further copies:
C80, C82, C83, C99, C100, C113, C117, C130, C131, C147, C148, C150, C165, C167, C168, C184, C185, C245, C248, C249, C250: 1uF 16V X7R; C_0603_1608Metric; MPN C0603C105K4RACTU
C96, C97, C114, C116, C133, C134, C151, C164, C181, C182, C246, C247, C251, C252: 100nF 50V X7R; C_0603_1608Metric; MPN C0603C104K5RACTU
D15, D16, D17, D18, D19, D20, D21, D22, D23, D24, D25, D26, D27, D28, D41, D42, D47, D48, D53, D54, D59, D60, D66, D71, D72, D77, D78, D79: 1N4448WS/BAS16J; D_SOD-323F; MPN BAS16J,115 / BAS16J,135
R56, R57, R63, R75, R90, R103, R118, R131, R146, R159, R261, R262, R265, R266: 470K; R_0805_2012Metric; MPN RK73H2ATTD4703F
R59, R60, R76, R89, R104, R117, R132, R145, R160, R260, R263, R264, R273, R274: 10K; R_0805_2012Metric; MPN RK73H2ATTD1002F
TP34, TP35, TP36, TP37, TP38, TP39, TP40, TP64, TP68, TP69, TP70, TP71, TP78, TP82, TP83, TP84, TP85, TP92, TP96, TP97, TP98, TP99, TP106, TP110, TP111, TP112, TP113, TP120, TP124, TP125, TP126, TP127, TP134, TP138, TP139, TP141, TP148, TP152, TP153, TP154, TP155, TP166: TestPoint; TestPoint_Pad_D1.5mm
U16, U27, U32, U36, U41, U74, U82: 74LVC2G06; SOT-23-6; MPN 74LVC2G06GV,125
U22, U31, U42, U72, U77, U80, U85: 74HC02; TSSOP-14_4.4x5mm_P0.65mm; MPN 74VHC02FT
U26, U37, U46, U75, U78, U83, U86: 74LVC2G17; SOT-23-6; MPN 74LVC2G17GV,125

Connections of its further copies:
+3V3: C80.2, C82.2, C83.2, C99.2, C100.2, C113.2, C117.2, C130.2, C131.2, C147.2, C148.2, C150.2, C165.2, C167.2, C168.2, C184.2, C185.2, C245.2, C248.2, C249.2, C250.2, U16.5 (VCC), U22.14 (VCC), U26.5 (VCC), U27.5 (VCC), U31.14 (VCC), U32.5 (VCC), U36.5 (VCC), U37.5 (VCC), U41.5 (VCC), U42.14 (VCC), U46.5 (VCC), U72.14 (VCC), U74.5 (VCC), U75.5 (VCC), U77.14 (VCC), U78.5 (VCC), U80.14 (VCC), U82.5 (VCC), U83.5 (VCC), U85.14 (VCC), U86.5 (VCC); also elsewhere on the board
/Channel 2/~Shutdown1: R56.2, TP36.1 (1_1), U16.6, U26.1; also elsewhere on the board
/Channel 2/~Shutdown2: R57.2, TP37.1 (1_1), U16.4, U26.3; also elsewhere on the board
/Channel 3/~Shutdown1: R63.2, TP64.1 (1_1), U37.1, U41.6; also elsewhere on the board
/Channel 3/~Shutdown2: R75.2, TP68.1 (1_1), U37.3, U41.4; also elsewhere on the board
/Channel 4/~Shutdown1: R90.2, TP78.1 (1_1), U36.6, U46.1; also elsewhere on the board
/Channel 4/~Shutdown2: R103.2, TP82.1 (1_1), U36.4, U46.3; also elsewhere on the board
/Channel 5/~Shutdown1: R118.2, TP92.1 (1_1), U74.6, U75.1; also elsewhere on the board
/Channel 5/~Shutdown2: R131.2, TP96.1 (1_1), U74.4, U75.3; also elsewhere on the board
/Channel 6/~Shutdown1: R146.2, TP106.1 (1_1), U27.6, U78.1; also elsewhere on the board
/Channel 6/~Shutdown2: R159.2, TP110.1 (1_1), U27.4, U78.3; also elsewhere on the board
/Channel 7/~Shutdown1: R261.2, TP120.1 (1_1), U82.6, U83.1; also elsewhere on the board
/Channel 7/~Shutdown2: R262.2, TP124.1 (1_1), U82.4, U83.3; also elsewhere on the board
/Channel 8/~Shutdown1: R265.2, TP134.1 (1_1), U32.6, U86.1; also elsewhere on the board
/Channel 8/~Shutdown2: R266.2, TP138.1 (1_1), U32.4, U86.3; also elsewhere on the board
/Shutdown_Global_Force: D15.1 (K), D16.1 (K), D17.1 (K), D18.1 (K), D19.1 (K), D20.1 (K), D21.1 (K), D22.1 (K), D23.1 (K), D24.1 (K), D25.1 (K), D26.1 (K), D27.1 (K), D28.1 (K); also elsewhere on the board
/~All_Amps_Disabled: D41.1 (K), D42.1 (K), D47.1 (K), D48.1 (K), D53.1 (K), D54.1 (K), D59.1 (K), D60.1 (K), D66.1 (K), D71.1 (K), D72.1 (K), D77.1 (K), D78.1 (K), D79.1 (K); also elsewhere on the board
/~Shutdown_Global_Sense: U22.3, U22.5, U31.3, U31.5, U42.3, U42.5, U72.3, U72.5, U77.3, U77.5, U80.3, U80.5, U85.3, U85.5; also elsewhere on the board
GND: C80.1, C82.1, C83.1, C96.2, C97.2, C99.1, C100.1, C113.1, C114.2, C116.2, C117.1, C130.1, C131.1, C133.2, C134.2, C147.1, C148.1, C150.1, C151.2, C164.2, C165.1, C167.1, C168.1, C181.2, C182.2, C184.1, C185.1, C245.1, C246.2, C247.2, C248.1, C249.1, C250.1, C251.2, C252.2, R56.1, R57.1, R63.1, R75.1, R90.1, R103.1, R118.1, R131.1, R146.1, R159.1, R261.1, R262.1, R265.1, R266.1, U16.2 (GND), U22.7 (GND), U26.2 (GND), U27.2 (GND), U31.7 (GND), U32.2 (GND), U36.2 (GND), U37.2 (GND), U41.2 (GND), U42.7 (GND), U46.2 (GND), U72.7 (GND), U74.2 (GND), U75.2 (GND), U77.7 (GND), U78.2 (GND), U80.7 (GND), U82.2 (GND), U83.2 (GND), U85.7 (GND), U86.2 (GND); also elsewhere on the board
unnamed: C96.1, D15.2 (A), R59.2
unnamed: C97.1, D16.2 (A), R60.2
unnamed: C114.1, D17.2 (A), R76.2
unnamed: C116.1, D18.2 (A), R89.2
unnamed: C133.1, D19.2 (A), R104.2
unnamed: C134.1, D20.2 (A), R117.2
unnamed: C151.1, D21.2 (A), R132.2
unnamed: C164.1, D22.2 (A), R145.2
unnamed: C181.1, D23.2 (A), R160.2
unnamed: C182.1, D24.2 (A), R260.2
unnamed: C246.1, D25.2 (A), R263.2
unnamed: C247.1, D26.2 (A), R264.2
unnamed: C251.1, D27.2 (A), R273.2
unnamed: C252.1, D28.2 (A), R274.2
unnamed: D41.2 (A), U22.8, U26.6
unnamed: D42.2 (A), U22.11, U26.4
unnamed: D47.2 (A), U72.8, U75.6
unnamed: D48.2 (A), U72.11, U75.4
unnamed: D53.2 (A), U80.8, U83.6
unnamed: D54.2 (A), U80.11, U83.4
unnamed: D59.2 (A), U85.8, U86.6
unnamed: D60.2 (A), U85.11, U86.4
unnamed: D66.2 (A), U42.8, U46.6
unnamed: D71.2 (A), U42.11, U46.4
unnamed: D72.2 (A), U31.8, U37.6
unnamed: D77.2 (A), U31.11, U37.4
unnamed: D78.2 (A), U77.8, U78.6
unnamed: D79.2 (A), U77.11, U78.4
unnamed: R59.1, TP34.1 (1_1), U22.6, U22.10
unnamed: R60.1, TP38.1 (1_1), U22.2, U22.13
unnamed: R76.1, TP39.1 (1_1), U31.6, U31.10
unnamed: R89.1, TP69.1 (1_1), U31.2, U31.13
unnamed: R104.1, TP70.1 (1_1), U42.6, U42.10
unnamed: R117.1, TP83.1 (1_1), U42.2, U42.13
unnamed: R132.1, TP84.1 (1_1), U72.6, U72.10
unnamed: R145.1, TP97.1 (1_1), U72.2, U72.13
unnamed: R160.1, TP98.1 (1_1), U77.6, U77.10
unnamed: R260.1, TP111.1 (1_1), U77.2, U77.13
unnamed: R263.1, TP112.1 (1_1), U80.6, U80.10
unnamed: R264.1, TP125.1 (1_1), U80.2, U80.13
unnamed: R273.1, TP126.1 (1_1), U85.6, U85.10
unnamed: R274.1, TP139.1 (1_1), U85.2, U85.13
unnamed: TP35.1 (1_1), U16.1, U22.4, U22.9
unnamed: TP40.1 (1_1), U31.4, U31.9, U41.1
unnamed: TP71.1 (1_1), U36.1, U42.4, U42.9
unnamed: TP85.1 (1_1), U72.4, U72.9, U74.1
unnamed: TP99.1 (1_1), U27.1, U77.4, U77.9
unnamed: TP113.1 (1_1), U80.4, U80.9, U82.1
unnamed: TP127.1 (1_1), U32.1, U85.4, U85.9
unnamed: TP141.1 (1_1), U16.3, U22.1, U22.12
unnamed: TP148.1 (1_1), U31.1, U31.12, U41.3
unnamed: TP152.1 (1_1), U36.3, U42.1, U42.12
unnamed: TP153.1 (1_1), U72.1, U72.12, U74.3
unnamed: TP154.1 (1_1), U27.3, U77.1, U77.12
unnamed: TP155.1 (1_1), U80.1, U80.12, U82.3
unnamed: TP166.1 (1_1), U32.3, U85.1, U85.12
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

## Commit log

2023-01-23 Initial commit of in-progress work from Dropbox shared folder
    [0 backplane pre channel shutdown logic copy-to-all.kicad_pcb, 0 pinout.ods, OCRA waveform generator step.ods, OCRA waveform generator.ods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]
2023-01-23 Removed extra files Deleted logs, backups, etc. created by KiCAD which shouldn't be in repo Added proper gitignore to keep these from coming back
    [0 backplane pre channel shutdown logic copy-to-all.kicad_pcb, backplane old 1st w per-channel logic on bot.kicad_pcb, backplane var0 2-wide orig.kicad_pcb, bac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]
2023-01-23 Started 7x6 16-channel connector board Adapted schem from 10x9 32-channel connector board Partial layout update, channel assignment silkscreen & routing TBD
    [output conn ODU 7x6 16ch.kicad_pcb, output conn ODU 7x6 16ch.kicad_sch]
2023-01-28 Migrated PCB designs to KiCAD 6
    [activity_indicator.kicad_sch, activity_indicator.sch, amp ctrl.kicad_sch, amp ctrl.sch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]
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2023-01-31 Schematic file fix, misc. PCB
    Fixed issue with KiCAD's automatic V5→V6 migration (corrected in 6.0.11) that caused problems with component references in multi-channel schematic sheets
    Finished migration in amp ctrl PCB, inc. re-assigning "exclude from BOM" attributes to testpoints, solder jumpers
    Added mounting hole to amp ctrl PCB for addl support to Ethernet jacks, power connector through stiffener
    [activity_indicator.kicad_sch, amp ctrl.kicad_sch, amp pwr.kicad_sch, amp_board_interface.kicad_sch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]
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2023-02-14 Ctrl board stiffener, ODU connector board
    Finished ctrl board stiffener, re-arranged output connector jumpers to fit cleanly without overlapping stiffener
    Re-named ODU 7x6 connector board for future "backwards direction pin-assignment" version, first-pass layout, added EMI caps
    [amp ctrl-User_StiffenerOutline.dxf, output conn ODU 7x6 16ch fwd.kicad_pcb, output conn ODU 7x6 16ch fwd.kicad_sch, output conn ODU 7x6 16ch.kicad_pcb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]
2023-05-03 New CS amp, misc. layout
    Changed current sense amp from INA828 to INA821/819 due to availability: schematic, layout for channel 1 (#6)
    Moved some thermistor components & ~Shutdown cap out of the way of the stiffener (#3)
    Updated footprints: SOD-323F for slightly larger solderable pads, SOIC-8 to remove excessive length on inside edge
    [amp ctrl.kicad_sch, channel.kicad_sch, digital.kicad_sch, digital_comms.kicad_sch]
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2023-05-03 New DAC
    Changed DAC from LTC2656 to AD5676 (#5)
    Changed digital Vdd for ADC to +3.3V
    Removed level translator ICs for +3.3V to +5V; no longer needed because AD5676 has separate analog and digital supply pins
    [amp ctrl.kicad_sch, digital.kicad_sch, digital_comms.kicad_sch]
2023-05-04 DRC fixes
    Deleted track stubs and overlapping vias, other misc. DRC fixes (#3)
    Shrank width of SOT-563 pads to fall within 0.16 mm clearance (6.3 mils)
    [amp ctrl.kicad_sch, channel.kicad_sch, digital.kicad_sch]
2023-05-04 Manufacturing fixes for amp control board
    Arranged *.Fab text for assembly drawings
    Minor stiffener outline fixes, silkscreen fixes
    Fixed missing BOM fields on some parts
    Removed exported manufacturing files from version control
    [amp ctrl BOM orig.xls, amp ctrl BOM.xls, amp ctrl.kicad_sch, amp pwr BOM.xls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]
2023-05-17 Corrected amp board ADC op-amp, created ODU connector 6x7 board
    Pared down list of ADC driver op-amps to list of ones tested
    Minor fixes to ODU 6x7 connector board (forward-pinned)
    Created duplicate of ODU 6x7 connector board, for reverse-pinned
    [amp ctrl.kicad_sch, digital.kicad_sch, output conn ODU 7x6 16ch bck.kicad_pcb, output conn ODU 7x6 16ch bck.kicad_sch]
2023-05-17 Serial interface speed improvement
    Upgraded serial interface to KiCAD 7.0
    Replaced USB-serial modules with higher-speed (12 Mbps) one (#7)
    [activity_indicator.kicad_sch, serial_interface.kicad_pcb, serial_interface.kicad_sch]
2023-08-22 Misc. mfg
    Marked top-side testpoints on amp control board as DNP
    Updated serial interface board's BOM-placement-help file
    Exported stiffener file for amp control board
    [amp ctrl-User_StiffenerOutline.dxf, amp ctrl.kicad_sch, channel.kicad_sch, digital.kicad_sch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]
2024-01-12 Upgraded to KiCAD 7.0 format Added 10µF cap to ADC's REFP pins to fix the voltage reference output (#15) Corrected ADC & DAC reset by adding a separate reset circuit (#14) Increased Cfbk compensation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
    [amp ctrl.kicad_sch, amp pwr.kicad_sch, channel.kicad_sch, digital.kicad_sch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]
2024-11-11 Amp ctrl: lengthened ADC & DAC reset delay to ~50 ms (#14) Backplane: added clock multiplier for 10 Mhz scanner clock (fixes #21) Backplane: reduced R5 from 10 to 1 ohm, to avoid excessive voltage dr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
    [activity_indicator.kicad_sch, amp ctrl.kicad_sch, amp_board_interface.kicad_sch, backplane.kicad_sch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]
2025-02-08 Comms fix, misc. improvements
    Added 33KΩ pull-ups & pull-downs to amp ctrl board's LVDS inputs, to solve issues caused by unconfigured FPGA pins during boot (fixes #23)
    Swapped backplane power input polarity for consistency with power connectors (fixes #20)
    Added "manual enable" optical input to backplane, for safety: requires positive enable to keep amplifiers enabled
    [0 pinout.ods, amp_board_interface.kicad_sch, backplane.kicad_sch, digital_comms.kicad_sch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]
2025-04-27 Corrected power-up behavior
    Backplane: Inverted polarity of Shutdown_Force (now Power_Enable_FPGA), to keep amps powered off until software starts: fixes #23
    Backplane: Routed Shutdown_Force to unused pin 3 on RJ45 jack B to amp boards: fixes #23
    Backplane: Added pull-up and pull-down resistors to fanout buffer inputs, to keep SCK & ~LDAC signals in proper state during power-on: fixes #23
    Amp control: Added transistor to reset DAC & ADC from pin 3 of RJ45 jack B
    [0 pinout.ods, activity_indicator.kicad_sch, amp ctrl.kicad_sch, amp_board_interface.kicad_sch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]
2025-04-30 Misc. cleanup for mfg & improvements
    Minor backplane pinout doc corrections (SCKO5 polarity, clarified some descriptions)
    Backplane: Added differential- and common-mode (to standoffs) power filtering, for EMI escaping over power wiring
    Amp ctrl: Changed DAC testpoints from individual pads to Keystone 5019 for easier probing
    Corrected part numbers, DNP vs. non-BOM-item indications, other misc. BOM issues
    [0 pinout.ods, amp ctrl.kicad_sch, amp_board_interface.kicad_sch, backplane.kicad_sch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]
2025-05-02 Backplane cleanup for mfg, schematic clarifications, added alt. power connectors
    [activity_indicator.kicad_sch, amp_board_interface.kicad_sch, backplane.kicad_sch, fanout_buffer.kicad_sch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]
2025-07-19 Updated KiCAD file versions to 9.0
    [activity_indicator.kicad_sch, amp ctrl.kicad_sch, amp pwr.kicad_pcb, amp pwr.kicad_sch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]
2025-07-19 Moved all project-specific symbols & footprints into new "shim" libraries Updated projects to reference the new "shim" library
    [activity_indicator.kicad_sch, amp ctrl.kicad_sch, amp pwr.kicad_pcb, amp_board_interface.kicad_sch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]
2025-07-19 Finished migrating footprint names
    [amp ctrl.kicad_sch, amp pwr.kicad_pcb, amp pwr.kicad_sch, amp_board_interface.kicad_sch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]
2025-07-19 Updated library references to 3D models, added 3D model directory & appropriate gitignore to omit proprietary models
    [digital_comms.kicad_sch]
2025-07-30 Added extra channels to fwd and bck boards
    [output conn ODU 7x6 16ch bck.kicad_pcb, output conn ODU 7x6 16ch bck.kicad_sch, output conn ODU 7x6 16ch fwd.kicad_pcb, output conn ODU 7x6 16ch fwd.kicad_sch]
2025-07-30 Added ODU footprints
    [output conn ODU 7x6 16ch bck.kicad_pcb, output conn ODU 7x6 16ch bck.kicad_sch, output conn ODU 7x6 16ch fwd.kicad_pcb, output conn ODU 7x6 16ch fwd.kicad_sch]
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2025-08-20 Danny Changes 2025 - Rev D2 of output connector board
    [output conn ODU 7x6 16ch bck.kicad_pcb, output conn ODU 7x6 16ch fwd.kicad_pcb]
2025-08-26 Functional fixes for ADC clk, +3.3V sag on backplane
    Amp ctrl: Added ADC clock inversion (fixes #34)
    Backplane: fixed series-resistor-induced voltage sag (fixes #33)
    [channel.kicad_sch, digital.kicad_sch, fpga.kicad_sch]
2025-10-16 BOM & reset fixes
    Amp ctrl: changed name of "Manufacturer" field to "MPN" to work with Aisler
    Amp ctrl: added part number to logic inverter, corrected various typos and part number problems
    Backplane: added pull-down to Shutdown_Reset signal (#35)
    Backplane: rethought Shutdown_Force circuit to make fail-safe (broken connections->shutdown), make work correctly (fixes #35)
    Backplane: updated/corrected various schematic annotations
    [amp ctrl.kicad_sch, amp_board_interface.kicad_sch, backplane.kicad_sch, channel.kicad_sch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]
2025-11-17 Added first draft of the optical control board (UART not included)
    [clock.kicad_sch, enable.kicad_sch, fiber_control_board.kicad_pcb, fiber_control_board.kicad_sch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]
2025-11-17 Added some silkscreen to the fiber control board
    [fiber_control_board.kicad_pcb]
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
